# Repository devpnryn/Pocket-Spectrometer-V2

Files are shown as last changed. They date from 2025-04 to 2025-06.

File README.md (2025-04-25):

# Pocket-Spectrometer-V2
<p float="left">
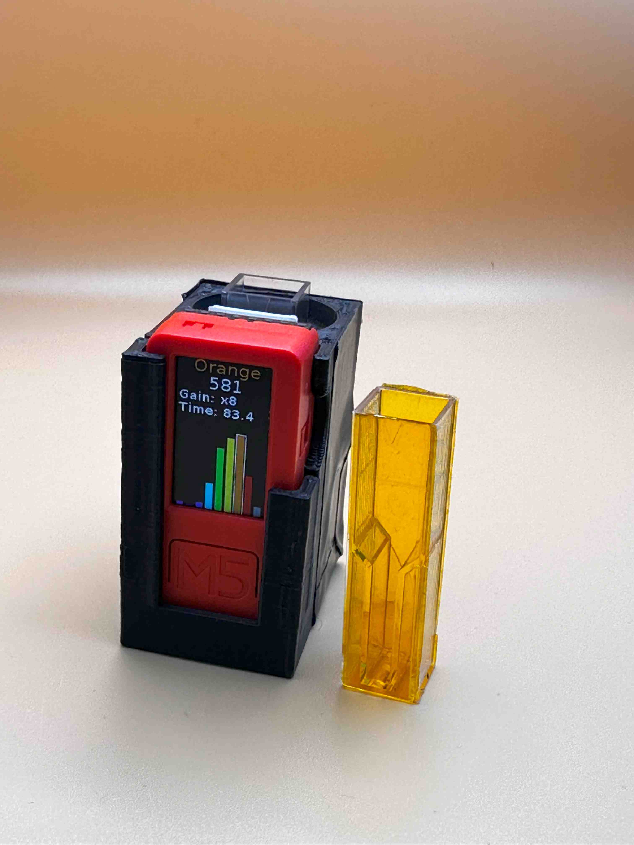
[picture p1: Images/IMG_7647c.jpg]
 
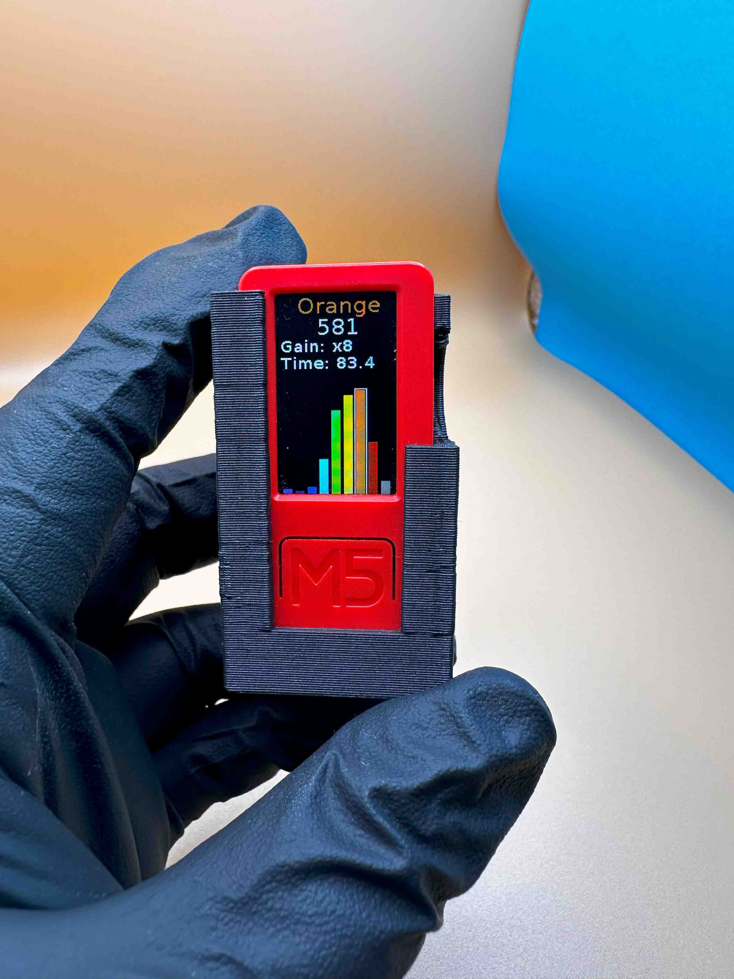
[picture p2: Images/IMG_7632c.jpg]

</p>   
I've always wanted to create a spectrometer that is so small it can fit into one's pocket and just barely larger than a cuvette itself. Working with bulky commercial spectrometers in labs, I was wondering about applications of such a small spectrometer. That's when I discovered the perfect combination – the M5StickC microcontroller and the AS7341 spectral sensor. My goal was simple: create an ultra-compact spectrometer that anyone could use. The first version of such miniature spectrometer is presented here: https://github.com/scientistnobee/Pocket-Spectrometer

This repository is the second version of the Pocket Spectrometer. The main improvement is the use of an AMS sensor from Adafruit that features a built-in grove-compatible port (known as Stemma QT) for I2C communication. While the previous version used a DFRobot AMS sensor that required manual soldering of I2C connections, this version simplifies assembly by using Adafruit's sensor with the Stemma port. The M5StickC and AMS sensor are connected using a Grove to Stemma connector, readily available from Adafruit. This cable offers improved stability with additional grip at the Grove port, making it more reliable than the original Grove cable used in the first version, which had a looser connection. This plug-and-play approach eliminates the need for soldering, reducing build steps and complexity. The 3D-printed main body has been modified to accommodate the Adafruit AMS sensor's different form factor. This version is improvement on the build side, but functionality of the spectrometer remains the same. 

## Bill of Materials (BOM)

* 1x M5StickC  (https://docs.m5stack.com/en/core/m5stickc_plus)
* 1x AS7341 spectral sensor from Adafruit (https://www.adafruit.com/product/4698)
* 1x 100mm Grove to stemma connector cable (https://www.adafruit.com/product/4528)
* 4x M2 screws  (https://eu.mouser.com/ProductDetail/Harwin/M80-2260000B?qs=DXv0QSHKF4wN5XPxPv8mDw%3D%3D&utm_source=octopart&utm_medium=aggregator&utm_campaign=855-M80-2260000B&utm_content=Harwin)
* 4x M2 heat-set inserts  (https://www.mouser.com/ProductDetail/SI/IUTFB-M2?qs=DPoM0jnrROVcA4QFWOCRzw%3D%3D&srsltid=AfmBOopUU4Yk4SA0-Q8_GQOYWdSUdiCuBDWbHyQfNmQKO6hRtp1Q_SV6)
* Black PLA filament for 3D printing of the enclosure and the cap
* White PLA for 3D printing of the reflector    
* * Black electrical tape

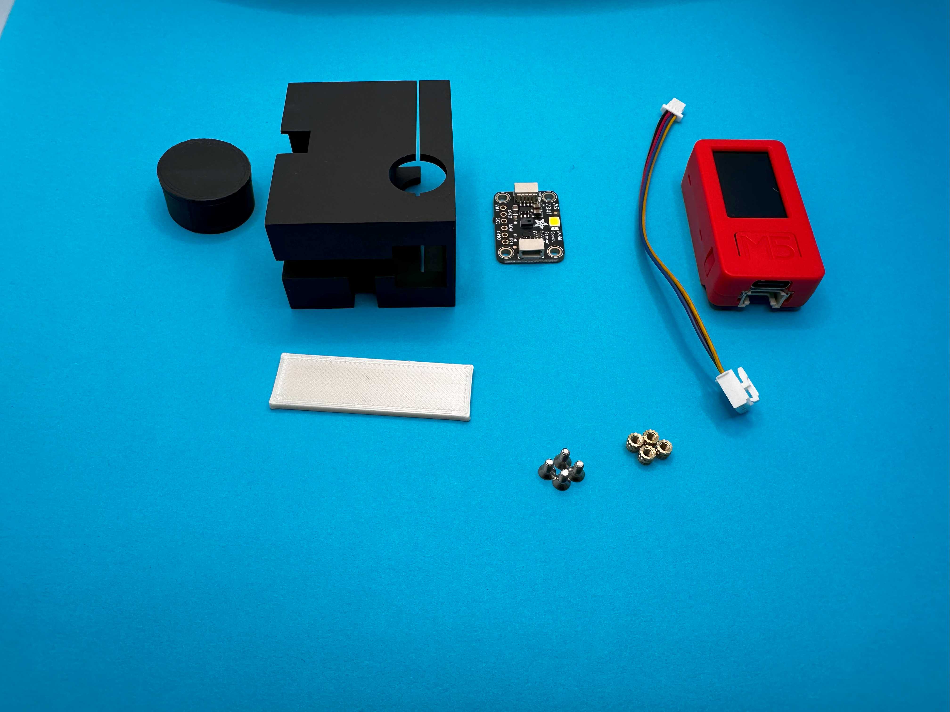
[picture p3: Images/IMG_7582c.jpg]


## 3D-Printed Components

* Main body  
* Cap 
* White reflector 

## Hardware Tools Required

* 3D printer  
* Soldering iron (for heat-set inserts only)
* M2 screwdriver

## Software Tools Required

* OpenSCAD for 3D printed parts (Optional, only required if you wany to modify the designs)  
* 3D printer slicer software (e.g., Ultimaker CURA)  
* Thonny IDE for programming the M5StickC

## Reasoning for Component Selection

### AS7341 Spectral Sensor: Advanced Spectral Sensing

The AS7341 sensor is crucial for this project:

* 11 readable individual sensor elements (10 light channels plus flicker detection)  
* Coverage from 350-1000 nm for comprehensive analysis  
* Built-in LED control for consistent illumination  
* Low power consumption for extended battery life  
* Affordable price point (~$16)
* Stemma QT connector for easy, solder-free connection

### M5StickC: Portable but Powerful Mini Computer

The M5StickC is the perfect platform for this project because it packs incredible functionality into a tiny package:

- Built-in rechargeable battery for true portability and field applications  
- USB-C connector for easy charging and programming  
- Seeed Grove port for simple sensor connections  
- Two user-programmable buttons for interface control  
- TFT display screen for displaying spectra in real-time   
- Beautifully labeled breakout header for expansion  
- Extra built-in sensors (6-axis IMU, Microphone, IR transmitter)   
- Compact size (48.2 x 25.5 x 13.7mm) ideal for portable spectrometer  
- MicroPython support for easy programming  
- Affordable price point (~$20)

## Build Instructions

### 1. Firmware Setup

#### Prepare M5StickC

1. Power on the M5StickC  
2. Quickly press the M5 button after restart (using reset/PWR button) until you see the settings screen
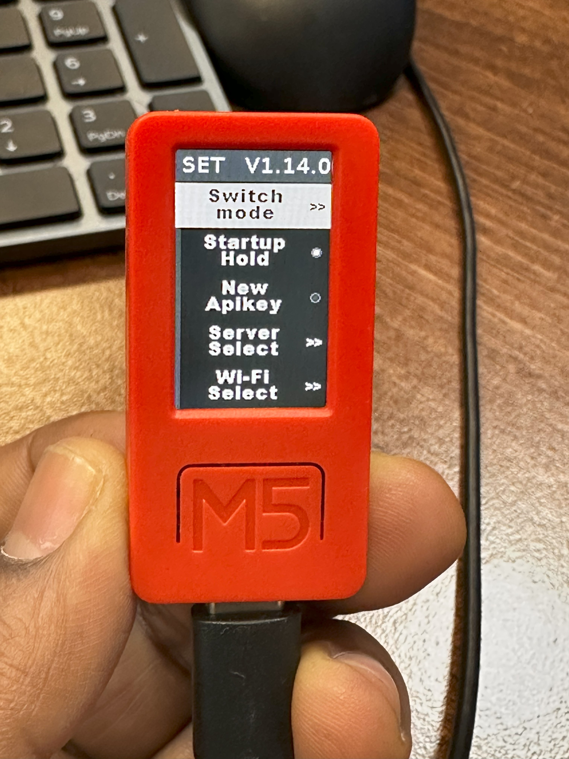
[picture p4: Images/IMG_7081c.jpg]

3. Select "Switch Mode" using the M5 button
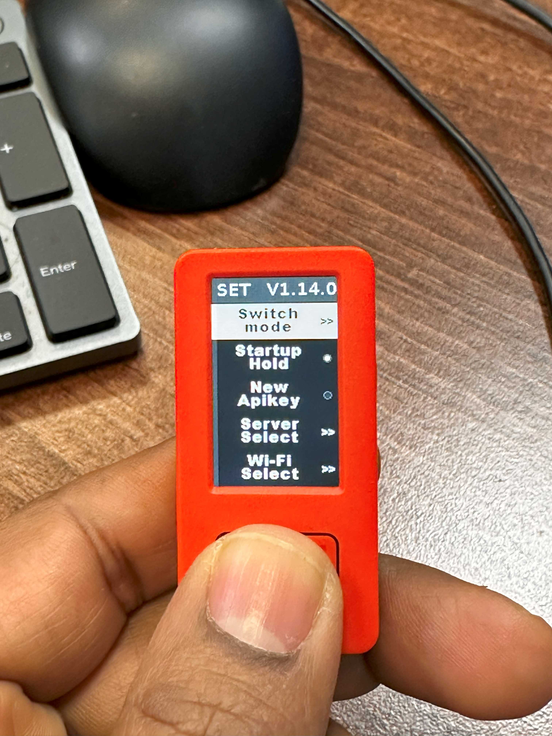
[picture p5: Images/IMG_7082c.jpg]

4. Choose "USB Mode" from the options
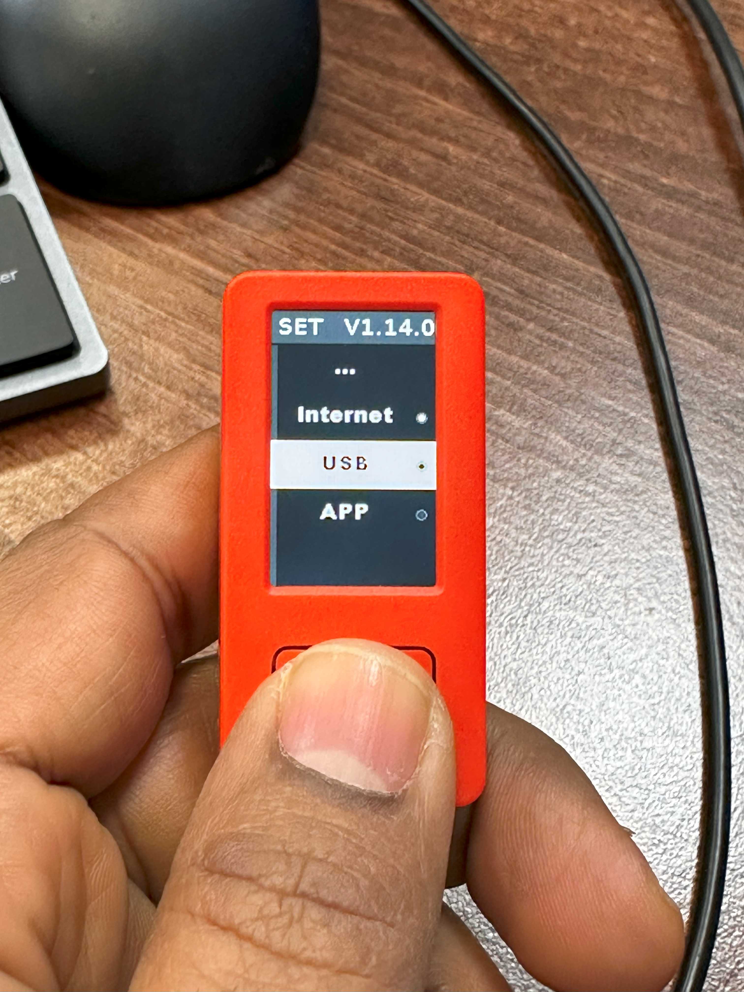
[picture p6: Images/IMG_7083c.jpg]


#### Set Up Thonny IDE and upload the firmware

1. Download and install [Thonny IDE](https://thonny.org/)  
2. Connect the M5stickC to computer and Open Thonny
4. Navigate to Tools > Options > Interpreter  
5. Configure settings:  
   - Set interpreter to "MicroPython (ESP32)"  
   - Select the correct COM port for your M5StickC  
   - Click OK and reconnect  
6. Once connected, you can write and test code directly in the IDE
7. Download the software from this repository and save into a folder (For example to Downloads folder).
8. Unzip the folder. Navigate to this folder's sub folder named Software inside Thorny. The files of the Software should should up at the top-left side as shown in the below figure.  
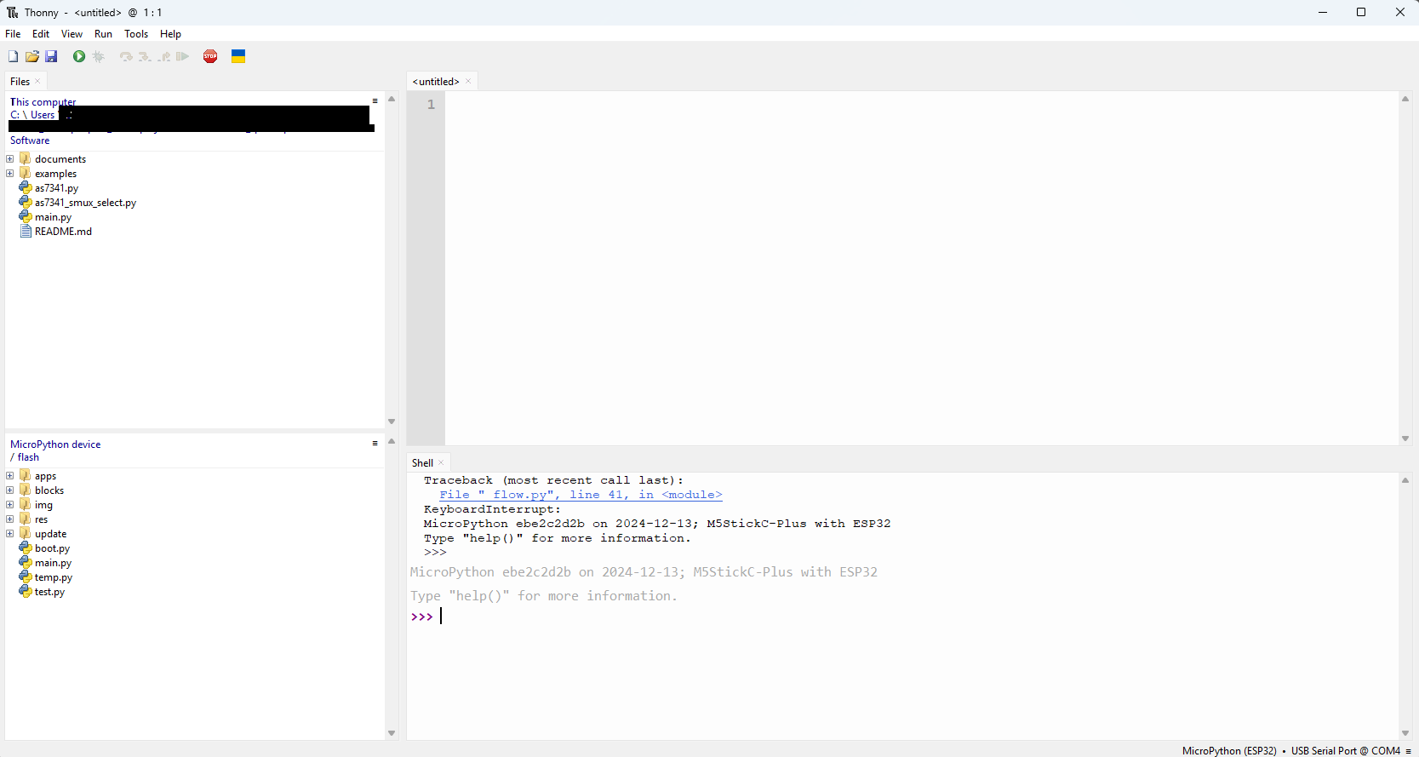
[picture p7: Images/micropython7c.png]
 
9. If M5StickC is connected and set-up correctly within Thorny then the existing files of M5stick's flash memoery can be seen at the lower left side of the Thorny.
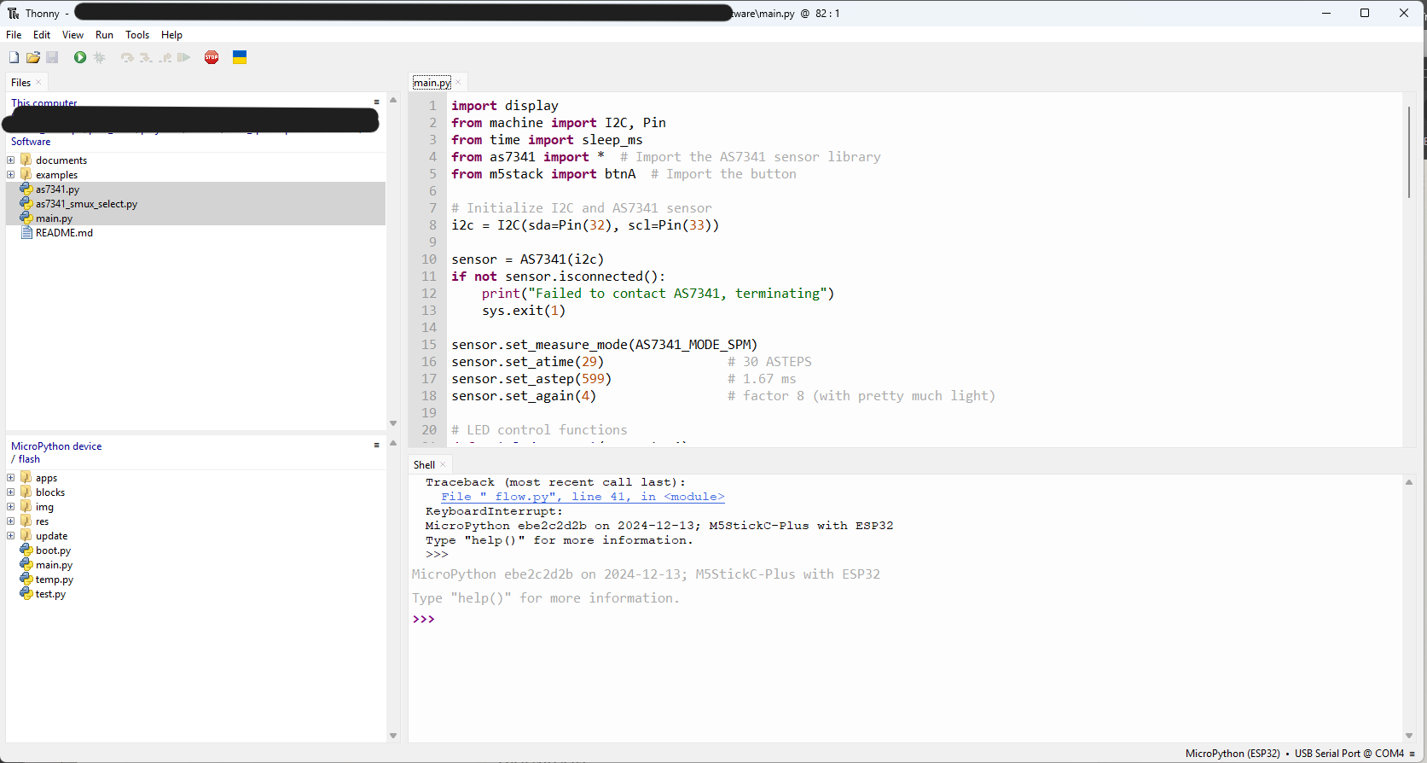
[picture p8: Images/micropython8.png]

11. Now copy (drag) the files from the computer (top left) to M5stickC (bottom-left).
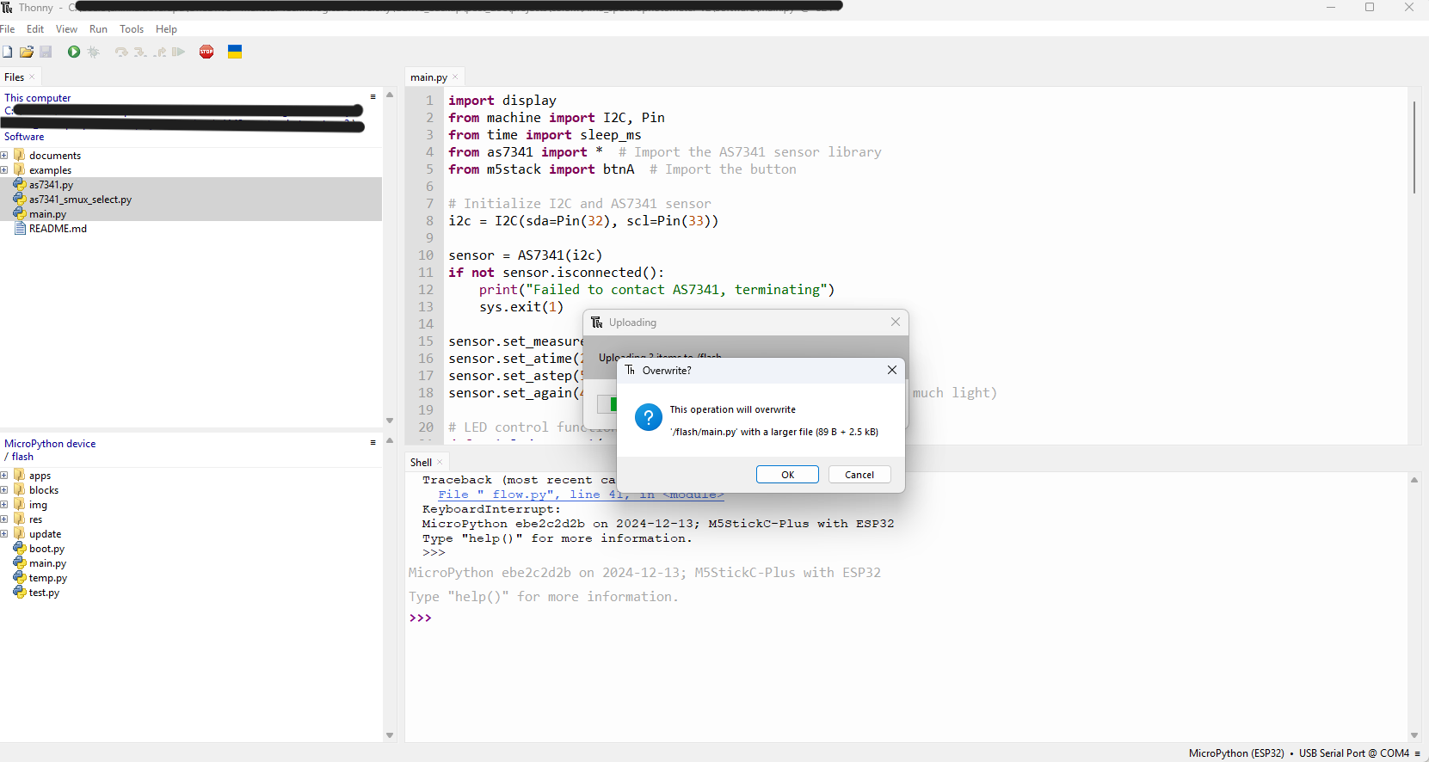
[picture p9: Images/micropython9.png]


### 2. Hardware Assembly

1. First test the components:
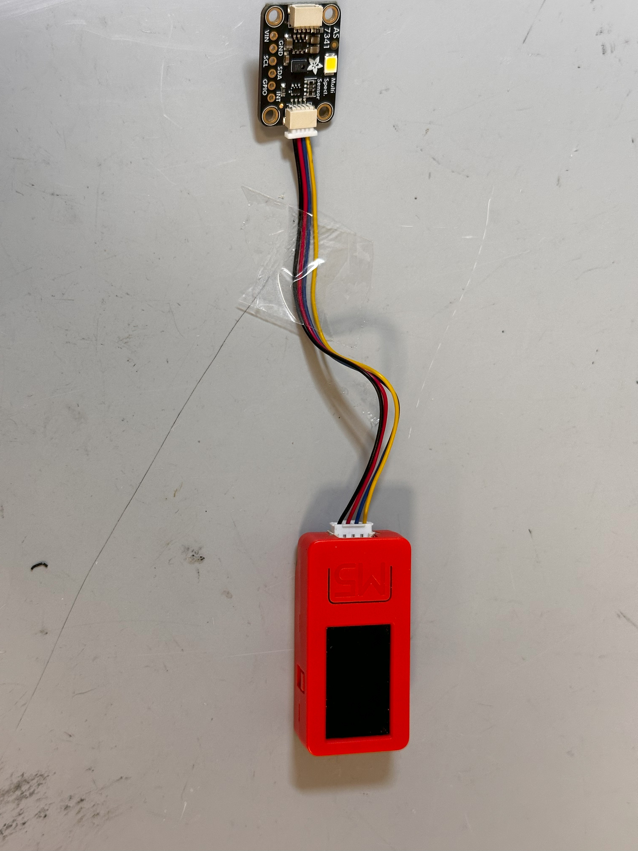
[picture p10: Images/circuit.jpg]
   - Connect the Grove to stemma cable between M5StickC and AMS sensor  
   - Upload the firmware using Thonny IDE as described above
   - Verify the spectral sensor functions correctly. If M5 button is pressed, white light of the AMS sensor should be on and a spectrum should be displayed on the screen as shown in the picture. 
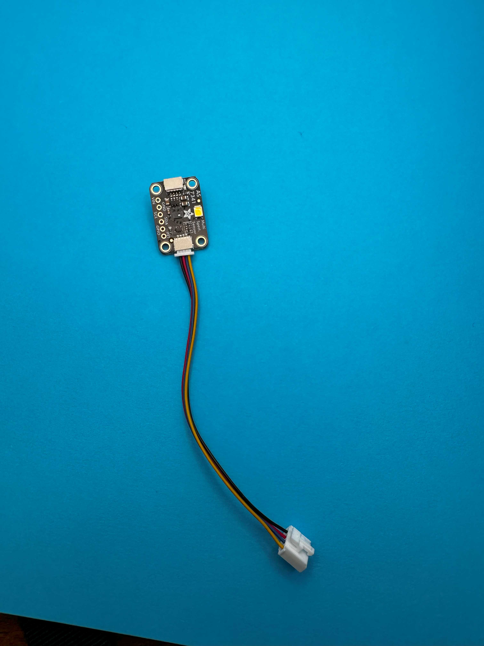
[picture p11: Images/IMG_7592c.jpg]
   - Disconnect the Grove connector cable from the M5StickC after the above testing  

2. Prepare the 3D printed parts:
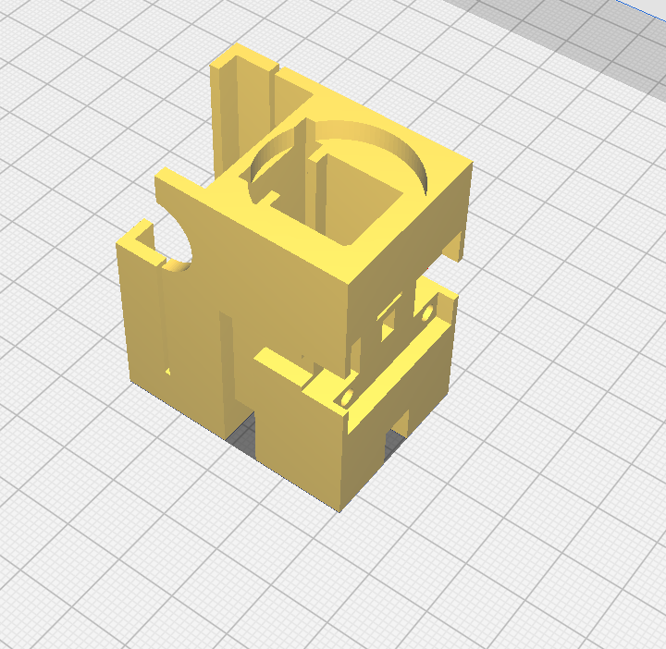
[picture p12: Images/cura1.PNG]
   - Print the main body and cap using Black PLA (no support required). Look here for the print orinetation 
   - Print the reflector using a white  PLA (no support required). Look here for the print orinetation 
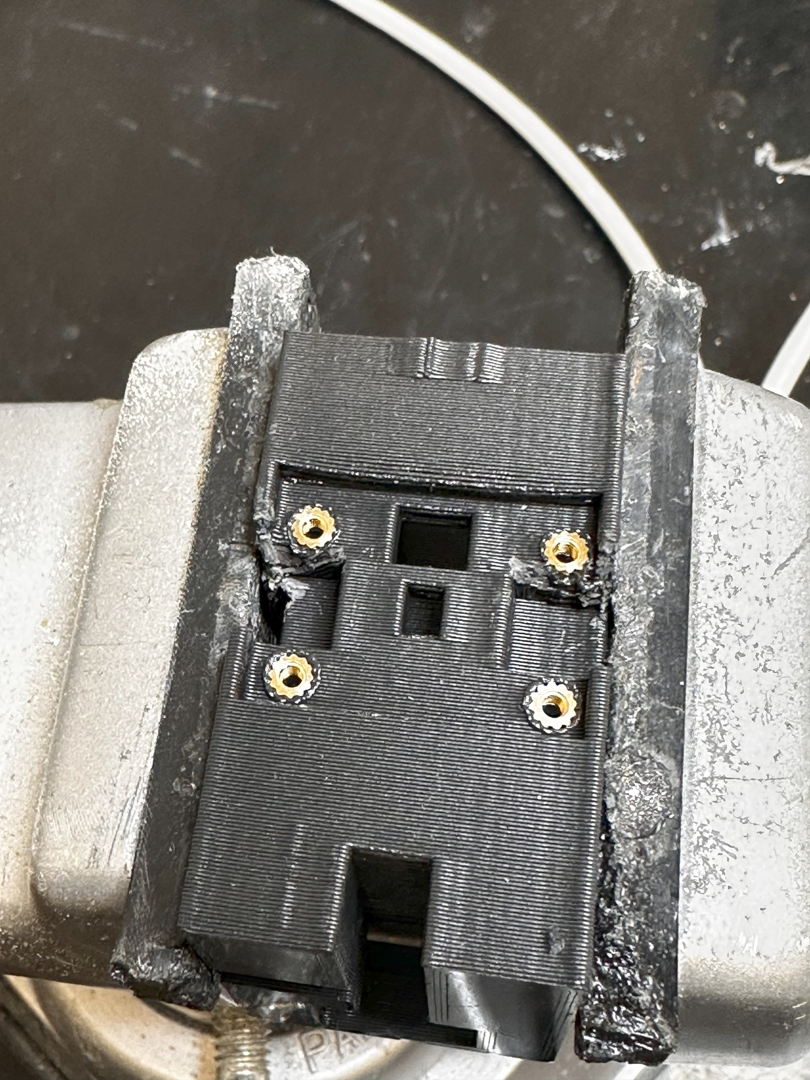
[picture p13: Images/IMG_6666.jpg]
   - Install M2 heat-set inserts into the main body using a soldering iron 
   
3. Final assembly:
   - Mount the AMS sensor to the body using M2 screws
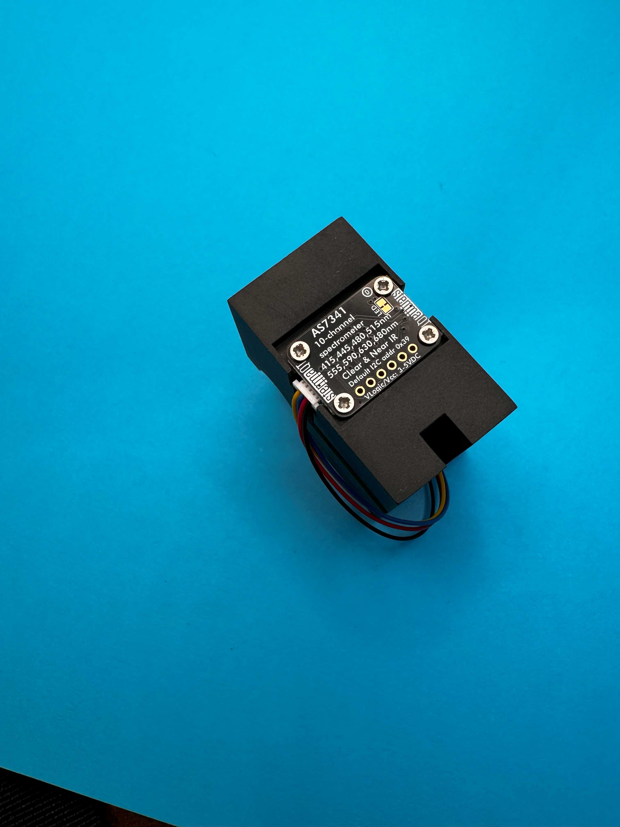
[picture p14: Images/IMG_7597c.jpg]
     
   - Route the Grove to stemma cable from the AMS sensor through the hole at the bottom into the slot for M5stickC as shown in the image here.
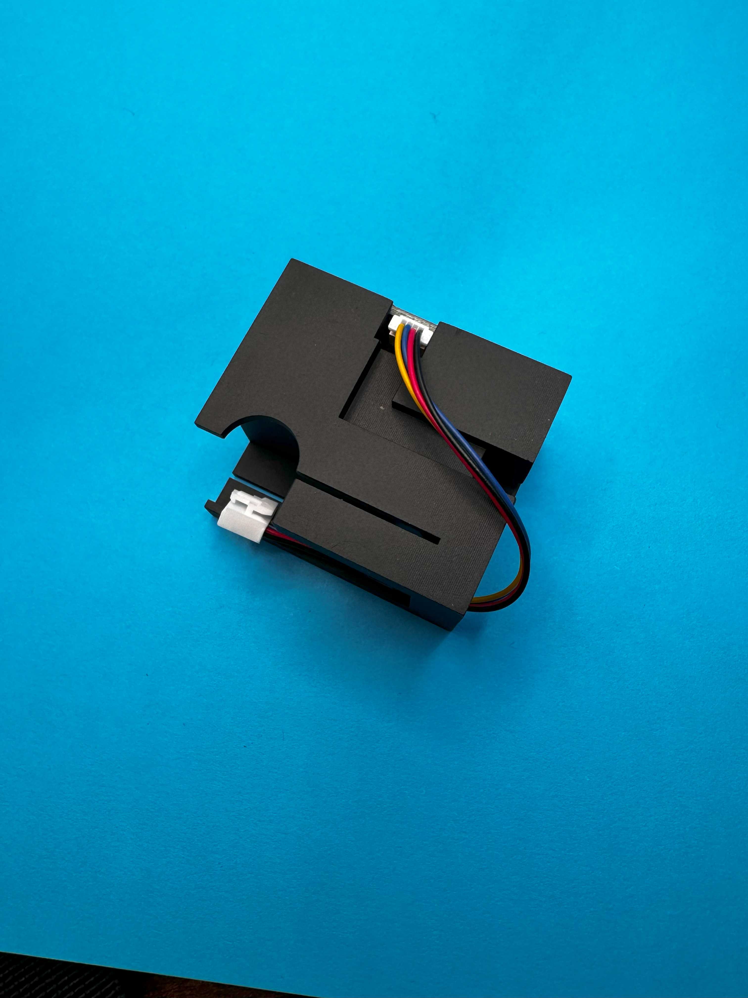
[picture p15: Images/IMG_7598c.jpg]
     
   - Connect the Grove to stemma cable to the M5StickC
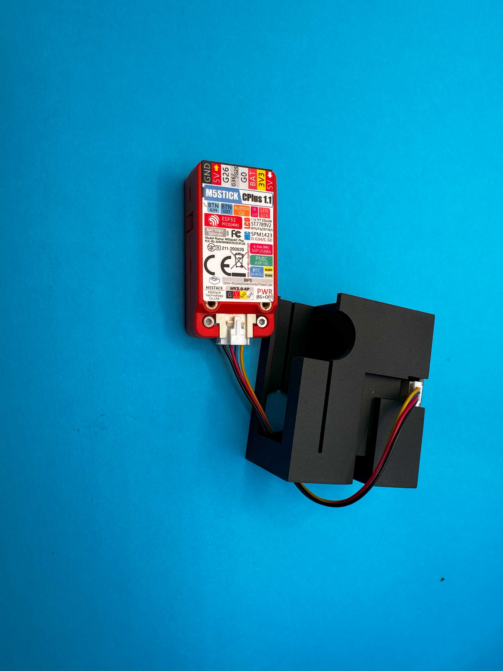
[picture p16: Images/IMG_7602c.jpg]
     
   - See this image for more clarity.
     
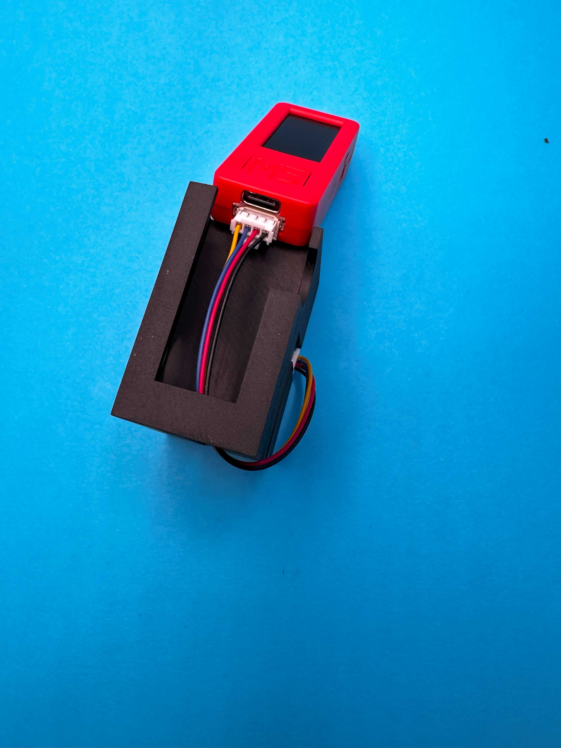
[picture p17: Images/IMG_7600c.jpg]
      
   - Press-fit the M5StickC into the body from the top
   - Apply black electrical tape to cover the AMS sensor and wires for light isolation and protection
   - Press fit the white reflector at the narrow slot.

## Applications

## Technical Implementation

The code is written in MicroPython for simplicity and accessibility, making it easy to modify for various applications. Most AI tools nowadays work well with Python code, making MicroPython an ideal choice for future modifications and improvements.

## Future Work

* Upgrade to AS7343 for expanded capabilities (14 spectral channels vs AS7341's 10 channels)  
* Optimize battery life for extended field use  
* Conduct comprehensive testing (Work in progress)
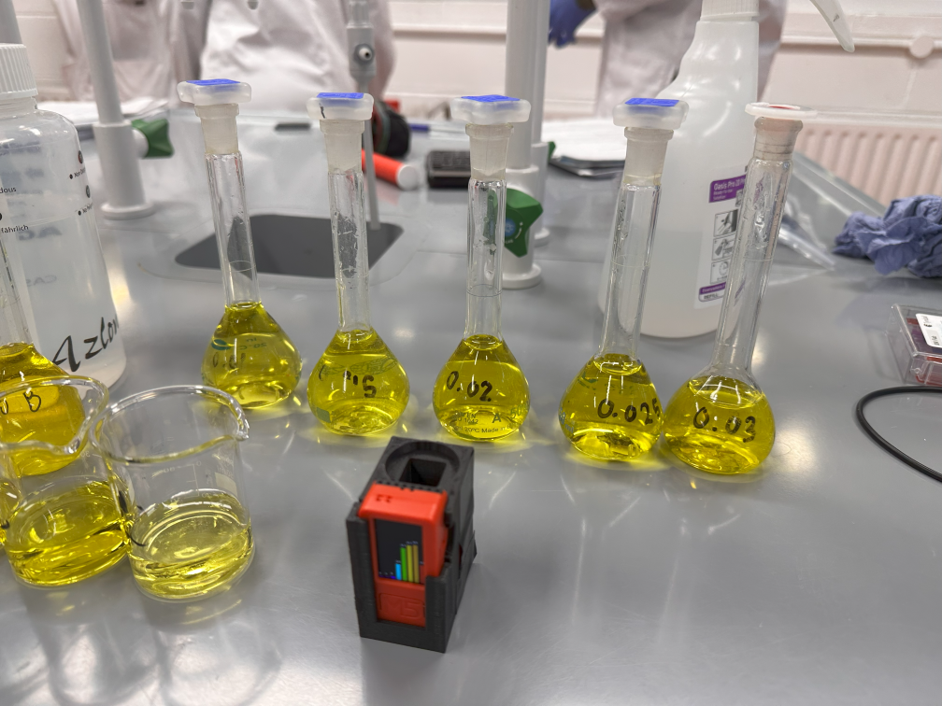
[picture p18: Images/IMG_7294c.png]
  
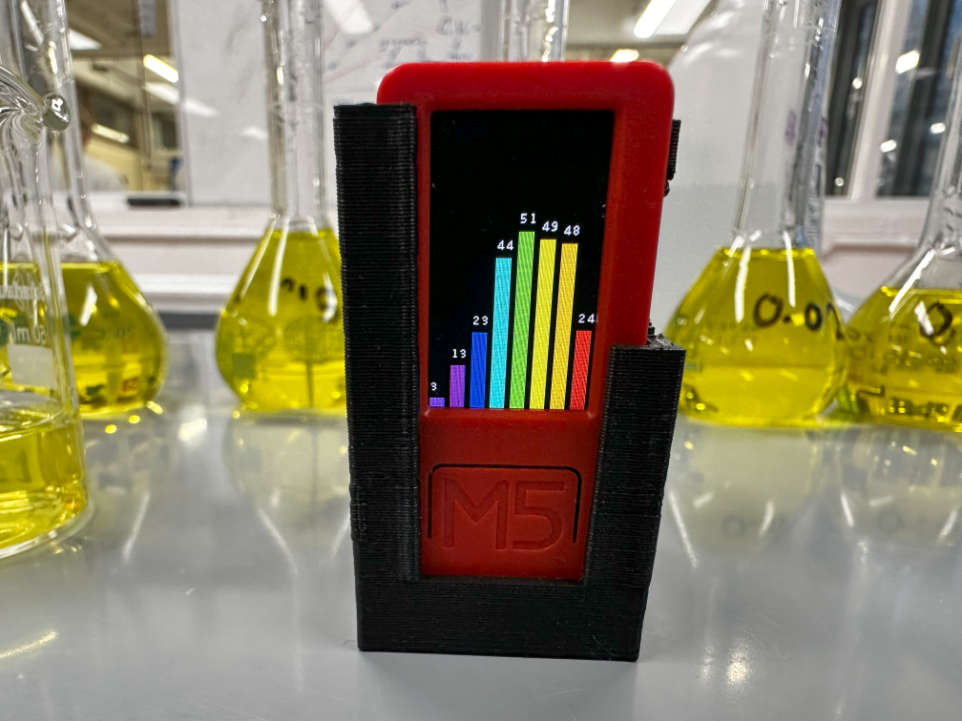
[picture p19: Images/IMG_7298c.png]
  
* Document detailed measurement protocols and generate standard curve plots  
* Add data logging functionality with time-stamped spectra files
* Create a calibration procedure for improved accuracy

## Troubleshooting Tips

### Software Issues

* If code doesn't execute properly, use the stop/rerun button in Thonny IDE until you see three forward-looking arrows in the console  
* Restart the device if experiencing connection issues  
* Ensure proper USB mode selection on the M5StickC before programming  
* Ensure correct serial port is selected at the Thonny IDE M

### Hardware Issues

* Verify the Grove to stemma cable is fully seated at both ends
* Ensure the M2 screws aren't overtightened on the sensor

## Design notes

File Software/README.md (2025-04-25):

# micropython-as7341

@Chinna Devarapu
- Adapted for M5StickC using bottom I2C sensor port
- Added LED control support for AS7341 sensor
- Added example for saving spectral data as text (save_data.py)
- Main functionality in main.py: displays spectral data as bar graph with count values above bars
- Developed using Thonny IDE

Original MicroPython driver by Rob Hamerling (Version 0.0, September 2022)
- Class for AS7341: 11 Channel Multi-Spectral Digital Sensor
- Adapted from WaveShare's Raspberry Pi implementation
- Source: https://www.waveshare.com/w/upload/b/b3/AS7341_Spectral_Color_Sensor_code.7z

## Modifications from Original
- Required specification of active I2C interface
- Pythonized implementation
- Optimized function names and I2C communications
- Improved code readability
- Added documentation strings

## Getting Started
- Use Micropython device with hardware I2C (e.g. ESP32)
- Connect AS7341 board via I2C interface
- Copy required files:
  - as7341.py
  - as7341_smux_select.py
- For GPIO examples: Connect GPIO pin to +3.3V (10K resistor) and pushbutton to GND

## Examples
- all_channels.py: read whole range of channels
- flicker.py: read flicker
- gpio_in_en.py: show use of GPIO pin for input
- interrupt.py: use of interrupt pin
- led_blink_pwm: show control of onboard LED
- pinint.py: use pin to trigger read-out
- syns.py: syns-mode, measurement starts with GPIO transition

## Documentation
- AS7341_AN000666_1-01.pdf - Application Note: SMUX Configuration
- AS7341_DS000504_3-00.pdf - Datasheet: 11-Channel Multi-Spectral Digital Sensor

Note: Repository is work in progress.

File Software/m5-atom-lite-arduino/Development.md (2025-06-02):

# Pocket Spectrometer for M5Atom Lite

This is a version of the Pocket Spectrometer project adapted for the M5Atom Lite
board. The device creates a WiFi access point and web server, allowing you to
control the AS7341 spectral sensor and view measurements through a web
interface.

## Hardware Requirements

- M5Atom Lite
- AS7341 Spectral Sensor
- Connecting wires

## Wiring

Connect the AS7341 sensor to the M5Atom Lite:

- SDA: GPIO 26
- SCL: GPIO 32
- VCC: 3.3V
- GND: GND

## Installation Instructions

1. Install the required libraries:
   - M5Atom (by M5Stack)
   - WiFi (included with ESP32)
   - WebServer (included with ESP32)
   - Wire (included with Arduino)

2. Copy all the project files to your Arduino project directory:
   - po_spectrometer_webserver.ino
   - AS7341.h
   - AS7341.cpp
   - html_content.h

3. Upload the code to your M5Atom Lite.

## Usage

1. Power on the M5Atom Lite.
2. The device will create a WiFi access point named "PocketSpectro" with
   password "spectro123".
3. Connect to this WiFi network with your phone, tablet, or computer.
4. Open a web browser and navigate to http://192.168.4.1
5. Use the web interface to take measurements and adjust settings.
6. Press the button on the M5Atom Lite to take a measurement directly from the
   device.

## LED Indicators

The RGB LED on the M5Atom Lite provides status information:

- **Purple**: Starting up
- **Green**: Sensor initialized successfully or measurement completed
- **Cyan**: Setting up WiFi
- **Red (blinking)**: Server running, ready for connections
- **Blue**: Measurement in progress
- **Red/Off alternating**: Sensor initialization error
- **Red/Blue alternating**: WiFi AP creation error

## Web Interface

The web interface allows you to:

- View spectral data as a bar chart
- Take new measurements
- Change the selected wavelength
- Adjust gain settings
- Adjust integration time
- Download measurement data as a text file

## Default Settings

- Gain: 8x
- Integration time: 83.4ms (ATIME=29)
- Default wavelength: Blue (480nm)

## Troubleshooting

- If the LED flashes red/off, there's an issue with the sensor connection. Check
  your wiring.
- If the LED flashes red/blue, there was a problem creating the WiFi access
  point. Try resetting the device.
- If you can't connect to the WiFi, ensure you're using the correct password and
  that you're within range.

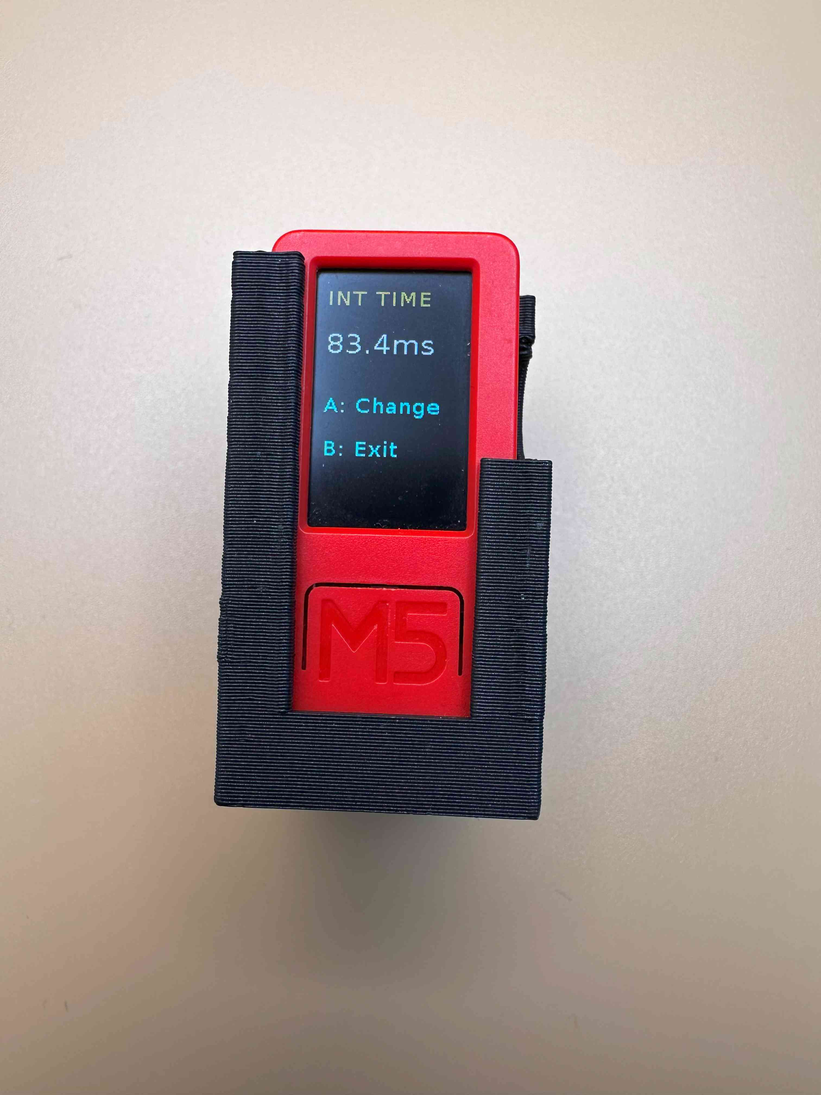
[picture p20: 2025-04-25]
Images/IMG_7650cd.jpg

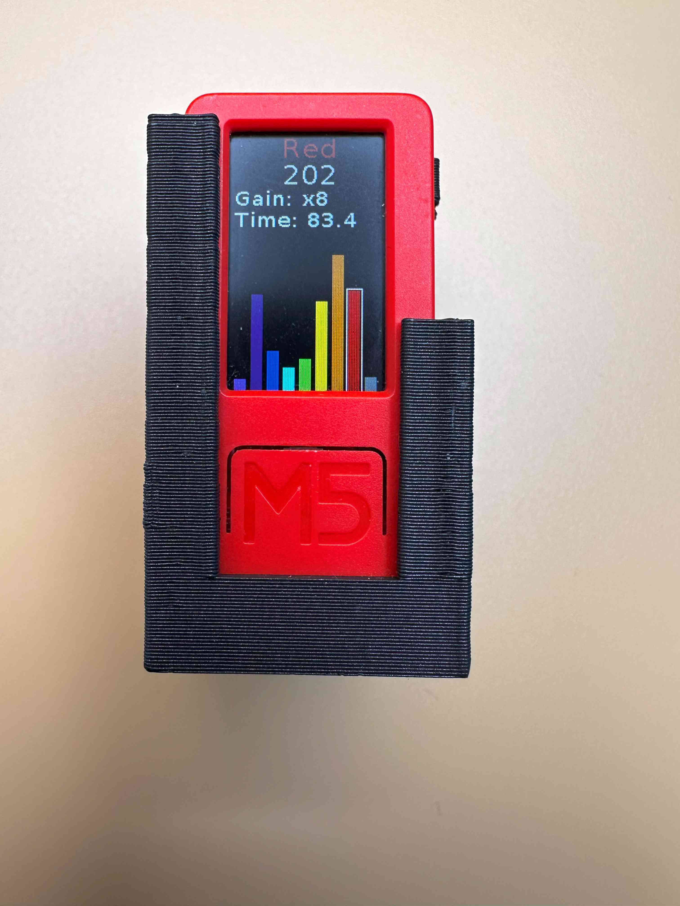
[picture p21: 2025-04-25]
Images/IMG_7651c.jpg

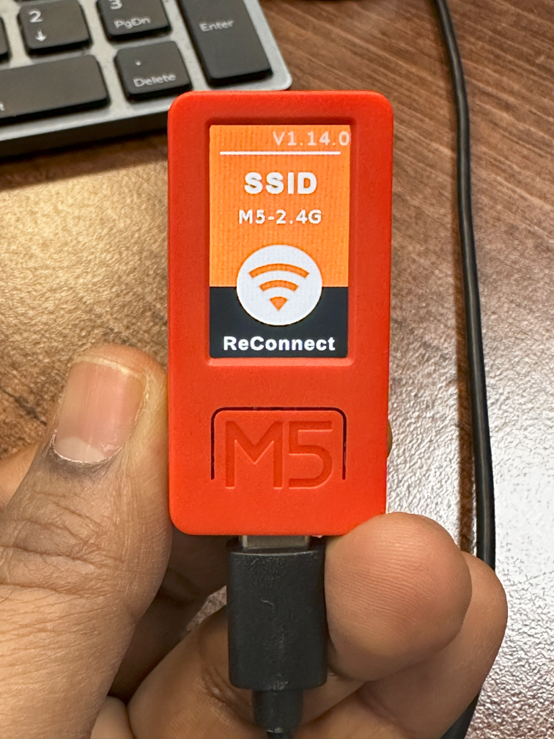
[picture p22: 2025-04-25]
Images/M5_1c.png

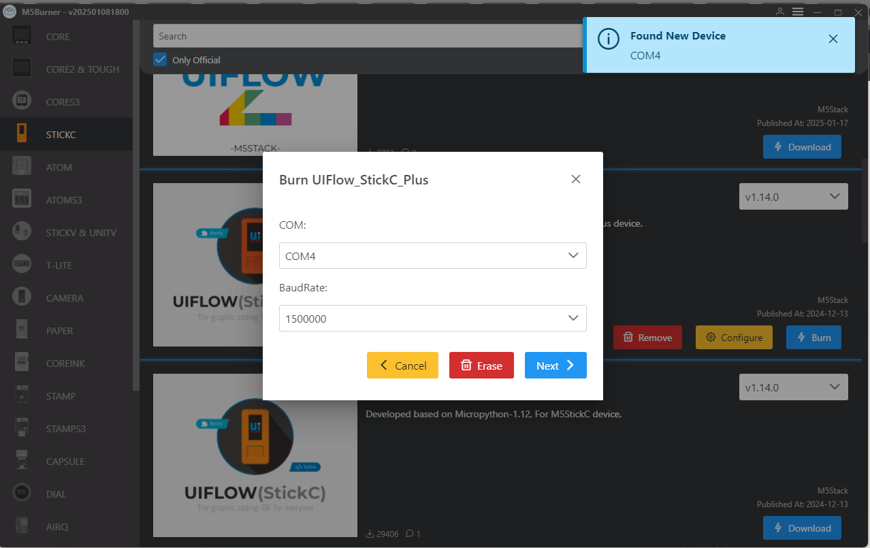
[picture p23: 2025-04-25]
Images/micropython5.png

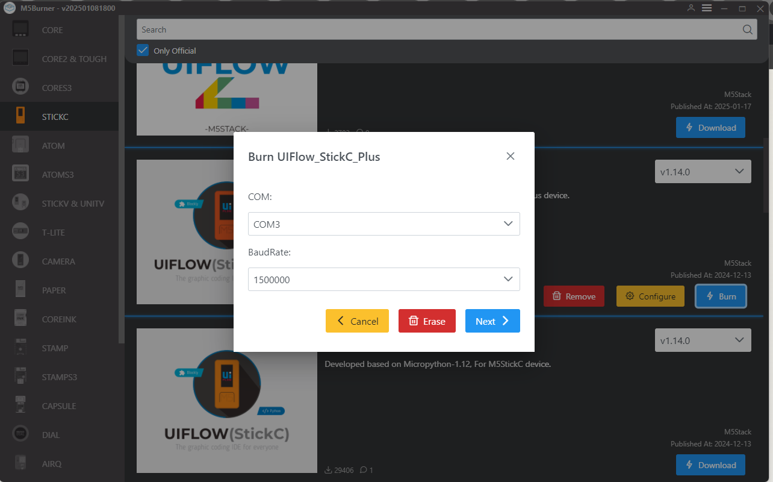
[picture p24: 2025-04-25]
Images/micropython2.png

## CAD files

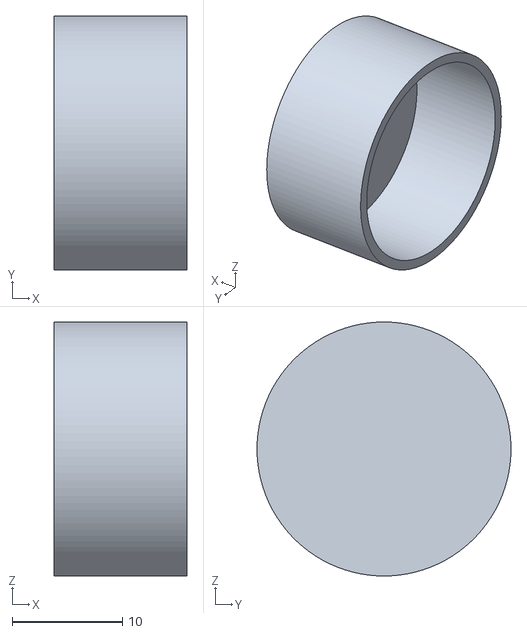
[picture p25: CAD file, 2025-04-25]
3D Design Files/STLs/Cap.stl
12.0 x 23.0 x 23.0

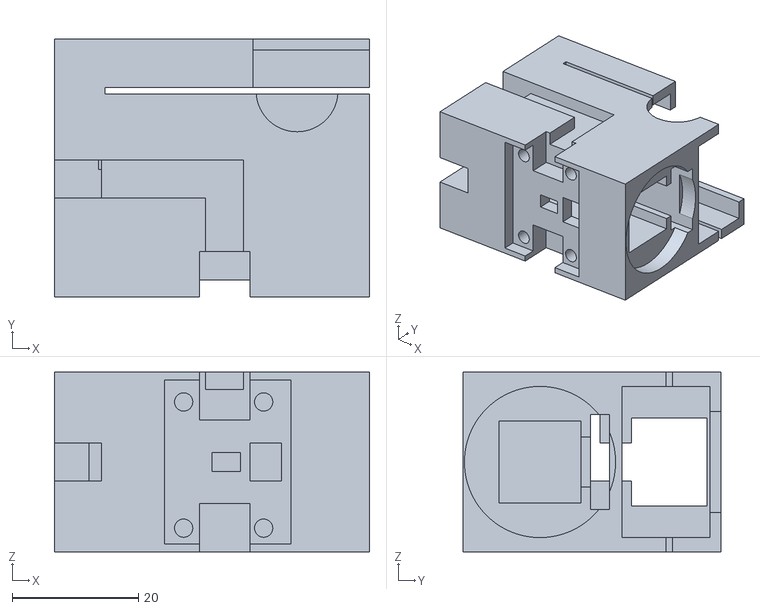
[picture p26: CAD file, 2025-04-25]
3D Design Files/STLs/Body.stl
50.0 x 41.0 x 28.5

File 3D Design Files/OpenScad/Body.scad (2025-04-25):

//color([0,0,1])
//translate([8.4,-24,12]) 
// rotate([90,90,180])
//import("AS7341.stl", convexity=3);


height_pd1=12;
height_pd=12;
 
$fn = 100; 
 w_m5=26.0;// width of m5stick
 h_m5=45;// height of m5stick
 t_m5=16; // thickness of m5stick
 wall=1.5; //wall of the body
 tol=0.5; //tolerance for printing
 //color([1,1,1], 0.5)
 difference(){
 union() {

     
      translate([0,0,0]) 
     cube ([h_m5,w_m5+tol+3,w_m5+tol+2], center=true);  //cuvette holder
     
           translate([-5,0,0]) 
     cube ([h_m5,w_m5+tol+3,w_m5+tol+2], center=true);  // extra cuvette holder bottom
     
     
       translate([0,18,0]) 
       cube ([h_m5, t_m5+tol, w_m5+tol+2], center=true);
     
            translate([-5,18,0]) 
       cube ([h_m5, t_m5+tol, w_m5+tol+2], center=true); //extra bottom part
   
 }
 union() {
      

      
 buttons_gap();     
          translate([21.0,-2.5,0])
     rotate([0,90,0])
     cylinder(d=24, h=4, center=true);// space for cap
     
  translate([-10,-13,-6.5])
rotate([90,0,0])
ada();   //space for AMS spectral sensor
     
           translate([-24.0,4,8]) 
            cube ([8, 6, 13], center=true);// for wiring4
    
             translate([-14.0,4,13]) 
            cube ([22, 6, 3], center=true);// for wiring3

      
                  translate([-0.5,-14,10]) 
            cube ([6, 6, 3], center=true);// for wiring3c
     
            translate([-0.5,-4,13]) 
            cube ([6, 22, 3], center=true);// for wiring2
     
           translate([-24.0,4,0]) 
            cube ([8, 40, 6], center=true);// for wiring1 bottom
     
     translate([4,-2.5,0]) 
          cube ([h_m5+tol,13.0,13.0], center=true); //cuvette
            color([1,0,0.5])
        translate([0.5,17.5,0]) 
            cube ([ h_m5, t_m5-wall-0.5, w_m5-wall-0.5], center=true);//m5stickc
            
translate([11.0,18,13]) 
cube ([8, 9, 3], center=true);// for m5 buttonB

 
 
 translate([-12,18,-13]) 
cube ([8, 9, 3], center=true);// for m5 buttonC
 
 
  translate([3,18,-13]) 
cube ([h_m5, 1, 3], center=true);// for m5 slit1


translate([3,18,13]) 
cube ([h_m5, 1, 3], center=true);// for m5 slit2
 
               color([0.5,0,0.5])
        translate([-20,18,0]) 
           cube ([20,12,14], center=true); 
     
        translate([3,28,0]) 
           cube([44,10,16], center=true);//oled screen
     
             translate([2,7,0]) 
     cube ([45,3,15], center=true);  //optical_filter
     
     
             translate([5,3,0]) 
           cube([40,8,8], center=true);//optical sensor window 
   
 }
 }


module buttons(){
 translate([-12,24,-12]) 
cube ([13, 13, 8], center=true);// button for m5 buttonC
 
 
 translate([14,24,13.15]) 
cube ([20, 13, 8], center=true);// for m5 buttonB
}


module buttons_gap(){
 translate([-12,18.0,-15]) 
cylinder(d=13, h=10);// button for m5 buttonC
 
 
 translate([11.0,18,7]) 
cylinder(d=13, h=10);// for m5 buttonB
    
    
     translate([14,24,11]) 
cube ([20, 13, 8], center=true);// for m5 buttonB
}






 module cap(){
difference(){
 union() {
 rotate([0,90,0])
         translate([0,0,0])
     cylinder(d=23.5, h=12, center=true);
     
 }

 union() {
              translate([-0.1,0.0,0.0])
 rotate([0,90,0])

     cylinder(d=20, h=12, center=true);
     }
 
 }
 }
 
//translate([30,-3,0])
//cap();
 
  //translate([-10,-12,-7])
//rotate([90,0,0])
//ams2();
 
 //buttons();
  
module ada(){
color([1,0,0])
union(){
    translate([0,-6.5,-1])
cube ([20.0,26.0,3.0]);  // PCB


    
color([0.4,0.6,0.1])
translate([3,-4.0,-8.0])
union(){
translate([0,0,0])
cylinder(d=2.9, h=10);//screw hole1

translate([12.7,0,0])
cylinder(d=2.9, h=10);//screw hole2
    
translate([0,20.03,0])
cylinder(d=2.9, h=10);//screw hole3

translate([12.7,20.03,0])
cylinder(d=2.9, h=10);//screw hole4   
    
}

color([0.4,0.6,0.5])

translate([0,5.5,-4.5])
union(){
    
    translate([7.5,-0.5,-2])
cube ([4.5,3,10]); //Ams sensor

    translate([13.5,-2,-2])    
cube ([5,6,10]); //LED
    
    
    
    translate([5.5,7.7,-1])    
cube ([8,8.5,10]); //Connector1 space    
    
    
     translate([5.5,-14.1,-1])    
cube ([8,8.5,10]); //Connector2 space       
    
}
}
}

//buttons();

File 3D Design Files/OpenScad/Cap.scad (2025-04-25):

height_pd1=12;
height_pd=12;
 
$fn = 100; 
 w_m5=26.0;// width of m5stick
 h_m5=45;// height of m5stick
 t_m5=16; // thickness of m5stick
 wall=1.5; //wall of the body
 tol=0.5; //tolerance for printing
 
 difference(){
 union() {

     
      translate([0,0,0]) 
     cube ([h_m5,w_m5+tol+3,w_m5+tol+2], center=true);  //cuvette holder
     
           translate([-5,0,0]) 
     cube ([h_m5,w_m5+tol+3,w_m5+tol+2], center=true);  //cuvette holder
     
     
       translate([0,18,0]) 
       cube ([h_m5, t_m5+tol, w_m5+tol+2], center=true);
     
            translate([-5,18,0]) 
       cube ([h_m5, t_m5+tol, w_m5+tol+2], center=true);
 }
 union() {
      

         
          translate([21.0,-2.5,0])
     rotate([0,90,0])
     cylinder(d=24, h=4, center=true);// space for cap
     
  translate([-10,-14.8,-7])
rotate([90,0,0])
ams2();   //space for AMS spectral sensor
     
           translate([-24.0,4,8]) 
            cube ([8, 6, 13], center=true);// for wiring4
    
             translate([-14.0,4,13]) 
            cube ([22, 6, 3], center=true);// for wiring3

      
                  translate([-0.5,-14,10]) 
            cube ([6, 6, 3], center=true);// for wiring3c
     
            translate([-0.5,-4,13]) 
            cube ([6, 22, 3], center=true);// for wiring2
     
           translate([-24.0,4,0]) 
            cube ([8, 40, 6], center=true);// for wiring1 bottom
     
     translate([4,-2.5,0]) 
          cube ([h_m5+tol,13.0,13.0], center=true); //cuvette
            color([1,0,0.5])
        translate([0.5,17.5,0]) 
            cube ([ h_m5, t_m5-wall-0.5, w_m5-wall-0.5], center=true);//m5stickc
            
translate([12,18,13]) 
cube ([8, 8, 3], center=true);// for m5 buttonB

 
 
 translate([-11,18,-13]) 
cube ([8, 8, 3], center=true);// for m5 buttonC
 
 
  translate([3,18,-13]) 
cube ([h_m5, 1, 3], center=true);// for m5 slit1


translate([3,18,13]) 
cube ([h_m5, 1, 3], center=true);// for m5 slit2
 
               color([0.5,0,0.5])
        translate([-20,18,0]) 
           cube ([20,12,14], center=true); 
     
        translate([3,28,0]) 
           cube([44,10,16], center=true);//oled screen
     
             translate([2,7,0]) 
     cube ([45,3,15], center=true);  //optical_filter
     
     
             translate([5,3,0]) 
           cube([40,8,8], center=true);//optical sensor window 
   
 }
 }


module ams1(){

union(){
    translate([0,0,-1])
cube ([22.5,20.5,2.0]);  // PCB


color([0.4,0.6,0.1])
translate([3.4,3,-2.0])
union(){
translate([0,0,0])
cylinder(d=2.9, h=10);//screw hole1

translate([15.1,0,0])
cylinder(d=2.9, h=10);//screw hole2
}
}
union(){


color([0.4,0.6,0.5])

translate([0,8.5,-2.5])
union(){
    
    translate([10-0.1,0,0])
cube ([2.2,3.5,4]); //Ams sensor
translate([6.1,0,0])    
cube ([1.5,3.5,4]); //LED1
    translate([14.1,0,0])    
cube ([1.5,3.5,4]); //LED2
    
}
}


}

module ams2(){

union(){
       translate([-1,0,-2])
cube ([22,16,5.0]);  // PCB

       translate([-1.0,12,-4.5])
cube ([18.5,4,3.0]);  // PCB holes 


}
union(){

    
color([0.4,0.6,0.1])
translate([2,2,-4.0])
union(){
translate([0,0,-2])
cylinder(d=3, h=10);//screw hole1

translate([14,0,-2])
cylinder(d=3, h=10);//screw hole2
}
color([0.4,0.6,0.5])

translate([0,5.5,-4.5])
union(){
    
    translate([8-0.1,0,-2])
cube ([2.3,4.5,10]); //Ams sensor
translate([4.3,0,-2])    
cube ([2.2,4.5,10]); //LED1
    translate([12.3,0,-2])    
cube ([2.2,4.5,10]); //LED2
    
}
}
}






 module cap(){
difference(){
 union() {
 rotate([0,90,0])
         translate([0,0,0])
     cylinder(d=23.5, h=12, center=true);
     
 }

 union() {
              translate([-0.1,0.0,0.0])
 rotate([0,90,0])

     cylinder(d=20, h=12, center=true);
     }
 
 }
 }
 
//translate([30,-3,0])
//cap();
 
  //translate([-10,-12,-7])
//rotate([90,0,0])
//ams2();
 
 

     

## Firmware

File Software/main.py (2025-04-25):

import display
from machine import I2C, Pin
from time import sleep_ms
from as7341 import *  # Import the AS7341 sensor library
from m5stack import btnA, btnB  # Import both buttons

# Initialize I2C and AS7341 sensor
i2c = I2C(sda=Pin(32), scl=Pin(33))

# Global variables for gain and integration time settings
gain_codes = [0, 1, 2, 3, 4, 5, 6, 7, 8, 9, 10]  # Gain codes (0-10)
gain_factors = [0.5, 1, 2, 4, 8, 16, 32, 64, 128, 256, 512]  # Corresponding gain factors
gain_index = 4  # Starting with gain factor 8 (index 4)
atime_settings = [9, 19, 29, 39, 49, 59]  # ATIME values for different integration times
atime_index = 2  # Starting with 29 (default value)
current_mode = 0  # 0 for normal mode, 1 for gain settings, 2 for integration time settings, 3 for wavelength selection
wavelength_index = 2  # Default to blue (index 2)
wavelength_names = ["Violet", "Vio-Blue", "Blue", "Cyan", "Green", "Yellow", "Orange", "Red", "NIR"]
wavelength_values = [415, 445, 480, 515, 555, 590, 630, 680, 940]  # Center wavelengths in nm

sensor = AS7341(i2c)
if not sensor.isconnected():
    print("Failed to contact AS7341, terminating")
    sys.exit(1)

sensor.set_measure_mode(AS7341_MODE_SPM)
sensor.set_atime(29)                # 30 ASTEPS (default)
sensor.set_astep(599)               # 1.67 ms
sensor.set_again(4)                 # factor 8 (default)

# LED control functions
def set_led_current(current_mA):
    """Set the LED current in mA (range: 0 to 100 mA)."""
    sensor.set_led_current(current_mA)

def enable_led(enable):
    """Enable or disable the onboard LED."""
    sensor.enable_led(enable)

# Create the TFT display object
tft = display.TFT()

# Define custom colors for spectral bands based on actual wavelengths
DEEP_VIOLET = 0x8000FF  # F1 (405-425nm)
VIOLET_BLUE = 0x4B0082  # F2 (435-455nm)
BLUE = 0x0000FF        # F3 (470-490nm)
CYAN = 0x00FFFF        # F4 (505-525nm)
GREEN = 0x00FF00       # F5 (545-565nm)
YELLOW = 0xFFFF00      # F6 (580-600nm)
ORANGE = 0xFF8000      # F7 (620-640nm)
DEEP_RED = 0xFF0000    # F8 (670-690nm)
GREY = 0x808080        # NIR (~940nm)

def update_settings():
    """Update sensor settings with current gain and integration time"""
    sensor.set_atime(atime_settings[atime_index])
    sensor.set_again(gain_codes[gain_index])  # Pass the gain code, not the factor

def display_gain_settings():
    """Display gain settings screen with larger font"""
    tft.clear(tft.BLACK)
    
    # Use larger font
    tft.font(tft.FONT_DejaVu18)
    
    # Display title
    tft.text(10, 20, "GAIN", tft.YELLOW)
    
    # Display current gain with large font
    tft.font(tft.FONT_DejaVu24)
    tft.text(10, 60, "x" + str(gain_factors[gain_index]), tft.WHITE)
    
    # Display simplified instructions with medium font
    tft.font(tft.FONT_DejaVu18)
    tft.text(10, 120, "A: Change", tft.CYAN)
    tft.text(10, 160, "B: Time", tft.CYAN)
    
def display_integration_settings():
    """Display integration time settings with larger font"""
    tft.clear(tft.BLACK)
    
    # Use larger font
    tft.font(tft.FONT_DejaVu18)
    
    # Display title
    tft.text(10, 20, "INT TIME", tft.YELLOW)
    
    # Display current integration time with large font
    tft.font(tft.FONT_DejaVu24)
    atime_ms = (atime_settings[atime_index] + 1) * 2.78  # Convert to milliseconds
    tft.text(10, 60, str(round(atime_ms, 1)) + "ms", tft.WHITE)
    
    # Display simplified instructions with medium font
    tft.font(tft.FONT_DejaVu18)
    tft.text(10, 120, "A: Change", tft.CYAN)
    tft.text(10, 160, "B: Exit", tft.CYAN)

def display_wavelength_selection():
    """Display wavelength selection with larger font"""
    tft.clear(tft.BLACK)
    
    # Use larger font
    tft.font(tft.FONT_DejaVu18)
    
    # Display title
    tft.text(10, 20, "WAVE LENT", tft.YELLOW)
    
    # Display selected wavelength with large font
    tft.font(tft.FONT_DejaVu24)
    tft.text(10, 60, wavelength_names[wavelength_index], tft.WHITE)
    tft.text(10, 95, str(wavelength_values[wavelength_index]) + " nm", tft.WHITE)
    
    tft.font(tft.FONT_DejaVu18)
    # Display simplified instructions
    tft.text(10, 140, "A: Change", tft.CYAN)
    tft.text(10, 180, "B: Gain", tft.CYAN)

def display_spectrum(f1, f2, f3, f4, f5, f6, f7, f8, nir):
    tft.clear(tft.BLACK)

    # Create space at top for headers (four lines of larger text)
    top_margin = 95  # Increased top margin for four text lines

    bars = [f1, f2, f3, f4, f5, f6, f7, f8, nir]  # Added NIR
    colors = [DEEP_VIOLET, VIOLET_BLUE, BLUE, CYAN, GREEN, YELLOW, ORANGE, DEEP_RED, GREY]  # Updated colors for accuracy
    wavelength_display = wavelength_values  # Use wavelength values defined globally

    # Get selected values first
    selected_bar = bars[wavelength_index]
    selected_color = colors[wavelength_index]
    selected_name = wavelength_names[wavelength_index]

    # Scale the values to fit on the screen
    max_val = max(bars)
    scale = (240 - top_margin - 20) / max_val if max_val > 0 else 1  # Adjusted for top margin and bottom labels

    # Adjust the bar width and spacing to fit the screen with 9 bars
    bar_width = 10  # Slightly smaller to fit NIR
    spacing = 4
    start_x = (135 - (9 * bar_width + 8 * spacing)) // 2

    for i, bar in enumerate(bars):
        height = int(bar * scale)
        color = colors[i]
        
        # Make the selected wavelength bar brighter
        if i == wavelength_index:
            # Draw a highlighted border for the selected wavelength
            tft.rect(start_x + i * (bar_width + spacing) - 2, 240 - height - 2, 
                     bar_width + 4, height + 4, tft.WHITE)
        
        # Draw the bar - adjust Y position for top margin
        tft.rect(start_x + i * (bar_width + spacing), 240 - height, 
                 bar_width, height, color, color)
        
        # Display wavelength value at the bottom with slightly larger font
        tft.font(tft.FONT_Default)  # Upgrade from DefaultSmall
        
        # For the visible wavelengths (0-7), show the value
        if i < 8:
            tft.text(start_x + i * (bar_width + spacing) - 2, 245, str(wavelength_values[i]), tft.WHITE)
        else:
            # For NIR, just display "NIR"
            tft.text(start_x + i * (bar_width + spacing) - 2, 245, "NIR", tft.WHITE)

    # Display the four information lines at the top with improved layout
    tft.font(tft.FONT_DejaVu24)
    
    # Line 1 - selected wavelength (centered, with color)
    name_width = len(selected_name) * 14  # Approximate width based on font
    center_x = (135 - name_width) // 2
    tft.text(center_x, 5, selected_name, selected_color)
    
    # Line 2 - count value (centered)
    count_width = len(str(selected_bar)) * 14  # Approximate width
    count_x = (135 - count_width) // 2
    tft.text(count_x, 30, str(selected_bar), tft.WHITE)
    
    # Switch to smaller font for lines 3 and 4
    tft.font(tft.FONT_DejaVu18)
    
    # Line 3 - gain information (left-aligned)
    tft.text(5, 55, "Gain: x" + str(gain_factors[gain_index]), tft.WHITE)
    
    # Line 4 - integration time (left-aligned, no units)
    atime_ms = (atime_settings[atime_index] + 1) * 2.78  # Convert to milliseconds
    tft.text(5, 75, "Time: " + str(round(atime_ms, 1)), tft.WHITE)

try:
    while True:
        if current_mode == 0:  # Normal measurement mode
            if btnA.wasPressed():  # Take measurement
                print("Taking measurement")
                set_led_current(25)
                enable_led(True)

                sensor.start_measure("F1F4CN")
                f1, f2, f3, f4, clr, nir = sensor.get_spectral_data()
                sensor.start_measure("F5F8CN")
                f5, f6, f7, f8, clr, nir = sensor.get_spectral_data()

                display_spectrum(f1, f2, f3, f4, f5, f6, f7, f8, nir)
                enable_led(False)
                
            elif btnB.wasPressed():  # Enter wavelength selection mode (changed order)
                current_mode = 3
                display_wavelength_selection()
                
        elif current_mode == 1:  # Gain settings mode
            if btnA.wasPressed():  # Cycle through gain settings
                gain_index = (gain_index + 1) % len(gain_codes)
                update_settings()
                display_gain_settings()
                
            elif btnB.wasPressed():  # Go to integration time settings mode
                current_mode = 2
                display_integration_settings()
                
        elif current_mode == 2:  # Integration time settings mode
            if btnA.wasPressed():  # Cycle through integration time settings
                atime_index = (atime_index + 1) % len(atime_settings)
                update_settings()
                display_integration_settings()
                
            elif btnB.wasPressed():  # Return to normal mode
                current_mode = 0
                tft.clear(tft.BLACK)
                
        elif current_mode == 3:  # Wavelength selection mode
            if btnA.wasPressed():  # Cycle through wavelengths
                wavelength_index = (wavelength_index + 1) % len(wavelength_names)
                display_wavelength_selection()
                
            elif btnB.wasPressed():  # Go to gain settings mode (changed order)
                current_mode = 1
                display_gain_settings()
        
        sleep_ms(100)

except KeyboardInterrupt:
    print("Interrupted from keyboard")

sensor.disable()

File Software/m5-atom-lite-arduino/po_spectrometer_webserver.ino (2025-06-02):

#include <M5Atom.h>
#include <WiFi.h>
#include <WebServer.h>
#include <Wire.h>
#include "html_content.h"
#include "AS7341.h"

// Access Point Configuration
const char *ap_ssid = "PocketSpectro";  // Name of the WiFi network the device will create
const char *ap_password = "spectro123"; // Password for the WiFi network (min 8 characters)
IPAddress local_ip(192, 168, 4, 1);     // Fixed IP address for the device
IPAddress gateway(192, 168, 4, 1);      // Gateway (same as IP)
IPAddress subnet(255, 255, 255, 0);     // Subnet mask

// Create web server object
WebServer server(80);

// Create AS7341 sensor object
AS7341 sensor;

// Global variables for gain and integration time settings
uint8_t gainCodes[] = {0, 1, 2, 3, 4, 5, 6, 7, 8, 9, 10};
float gainFactors[] = {0.5, 1, 2, 4, 8, 16, 32, 64, 128, 256, 512};
int gainIndex = 4; // Starting with gain factor 8 (index 4)
uint8_t atimeSettings[] = {9, 19, 29, 39, 49, 59};
int atimeIndex = 2;      // Starting with 29 (default value)
int wavelengthIndex = 2; // Default to blue(index 2)
String wavelengthNames[] = {"Violet", "Vio-Blue", "Blue", "Cyan", "Green", "Yellow", "Orange", "Red", "NIR"};
int wavelengthValues[] = {415, 445, 480, 515, 555, 590, 630, 680, 940}; // Center wavelengths in nm

// Spectral data storage
uint16_t spectralData[9]; // F1-F8 + NIR

// Flag to indicate if a new measurement was taken
bool newMeasurementTaken = false;

// LED status indicators
bool isServerRunning = false;
bool isMeasurementInProgress = false;
unsigned long lastLedUpdate = 0;
const int ledBlinkInterval = 500; // Blink interval in ms
bool ledState = false;

// Button debounce variables
unsigned long lastButtonPress = 0;
const int debounceTime = 300; // Debounce time in ms

// Function to update sensor settings
void updateSettings()
{
    sensor.setATime(atimeSettings[atimeIndex]);
    sensor.setGain(gainCodes[gainIndex]);

    // Debug output
    Serial.print("Updated settings - Gain: x");
    Serial.print(gainFactors[gainIndex]);
    Serial.print(", Integration time: ");
    float integrationTimeMs = (atimeSettings[atimeIndex] + 1) * 2.78;
    Serial.print(integrationTimeMs);
    Serial.println("ms");
}

// Function to take a measurement
void takeMeasurement()
{
    // Set measurement in progress flag
    isMeasurementInProgress = true;

    // Show measurement in progress with LED
    M5.dis.drawpix(0, 0x0000FF); // Blue color during measurement

    // Update sensor settings first
    updateSettings();

    // Turn on LED for measurement
    sensor.enableLED(true);
    sensor.setLEDCurrent(25); // 25mA current

    Serial.println("Starting first measurement (F1F4CN)...");

    // First measurement: F1-F4 + Clear + NIR
    sensor.startMeasure("F1F4CN");

    // Read the spectral data for first 4 channels
    uint16_t channelData1[6];
    sensor.getSpectralData(channelData1);

    Serial.println("First measurement data:");
    for (int i = 0; i < 6; i++)
    {
        Serial.print(i);
        Serial.print(": ");
        Serial.println(channelData1[i]);
    }

    Serial.println("Starting second measurement (F5F8CN)...");

    // Second measurement: F5-F8 + Clear + NIR
    sensor.startMeasure("F5F8CN");

    // Read the spectral data for next 4 channels
    uint16_t channelData2[6];
    sensor.getSpectralData(channelData2);

    Serial.println("Second measurement data:");
    for (int i = 0; i < 6; i++)
    {
        Serial.print(i);
        Serial.print(": ");
        Serial.println(channelData2[i]);
    }

    // Turn off LED after measurement
    sensor.enableLED(false);

    // Map to our spectral data array (F1-F8 + NIR)
    for (int i = 0; i < 4; i++)
    {
        spectralData[i] = channelData1[i];     // F1-F4
        spectralData[i + 4] = channelData2[i]; // F5-F8
    }

    // Use NIR from second measurement (or average both if preferred)
    spectralData[8] = channelData2[5]; // NIR

    // Debug output
    Serial.println("Final Spectral Data:");
    for (int i = 0; i < 9; i++)
    {
        Serial.print(wavelengthValues[i]);
        Serial.print("nm: ");
        Serial.println(spectralData[i]);
    }

    // Set flag to indicate new measurement
    newMeasurementTaken = true;

    // Measurement complete
    isMeasurementInProgress = false;

    // Show success with green LED for a moment
    M5.dis.drawpix(0, 0x00FF00); // Green color for success
    delay(500);

    // Return to server running indication
    if (isServerRunning)
    {
        M5.dis.drawpix(0, 0xFF0000); // Red color for server running
    }
}

// Function to handle DNS requests for captive portal
void handleDNS()
{
    // Redirect all domains to our web server
    server.sendHeader("Location", String("http://") + WiFi.softAPIP().toString(), true);
    server.send(302, "text/plain", "");
}

// HTTP request handlers
void handleRoot()
{
    server.send(200, "text/html", index_html);
}
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

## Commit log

2025-04-25 Initial commit without sensitive data
    [Body.scad, Body.stl, Cap.scad, Cap.stl]
2025-05-10 update device UI to prortrait mode with legible font size
2025-06-02 m5 atom board spectrometer
2026-02-02 update: - support for m5 stcikc plus 2 device - testing files added - docs updated.
